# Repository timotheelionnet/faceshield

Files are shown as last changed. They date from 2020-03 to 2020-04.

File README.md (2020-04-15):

# faceshield

3D printing models for faceshields built at NYU for NYU Langone Health
These models are based on the budmen design  https://budmen.com/ with modifications 
for comfort and durability based on NYU Langone Health ICU and Emergency Medicine staff.
Design Team: Mihály Vöröslakos, Neta Agmon, Victoria Bill, Elizabeth New, Benjamin King and Timothee Lionnet based on the budmen model.

Assembly requires:
- 1 3D printed shield holder (shield_holder_nyu)
- 1 3D printed strap lock (strap-lock)
- 1 transparent shield (we have used 0.5 mm thick carbonate sheets, cut pattern in transparent_shield_cut_nyu)
- 1 elastic band (0.5" wide)
- 1 piece of foam (3/4" wide by 0.5" thick weather stripping foam; about 9" per shield)
- 4 pop rivets (1/8" diameter, 1/8" grip length)

Instructions:
- 3D print the shield holder and its strap lock. 0.3 mm thick layers, 10% infill with 2 solid layers at the top and bottom work well for us. Using a 0.8 mm nozzle reduces print time more than 2-fold compared to 0.4 mm.
- cut the carbonate sheet (following the pattern in transparent_shield_cut_nyu). We have used laser cutting and other tools.
- cut a 9" long foam strip and stick it to the inside part of the shield holder.
- using a riveter, secure foam to shield holder with four pop rivets.
- cut desired length of elastic band and tighten using the strap lock.
- wipe assembly with Isopropyl Rubbing Alcohol 70% Wipe.

Detailed Materials and Assembly Instructions are available in pdf format:
Reusable  Face Shield Assembly NYU 204_13_20.pdf

Contact/Affiliations:

Benjamin King, PhD & Timothee Lionnet, PhD
Institute for Systems Genetics & Department of Cell Biology
NYU School of Medicine
http://www.timotheelionnet.net/

Neta Agmon, PhD 
Neochromosome, Inc. 
ACLSW 14th Floor 
430 East 29th street 
New York, NY 10016

Elizabeth New & Victoria Bill
NYU Tandon MakerSpace
https://engineering.nyu.edu/research-innovation/makerspace
tandon-makerspace@nyu.edu

Mihály Vöröslakos, PhD
Neuroscience Institute, 
NYU School of Medicine

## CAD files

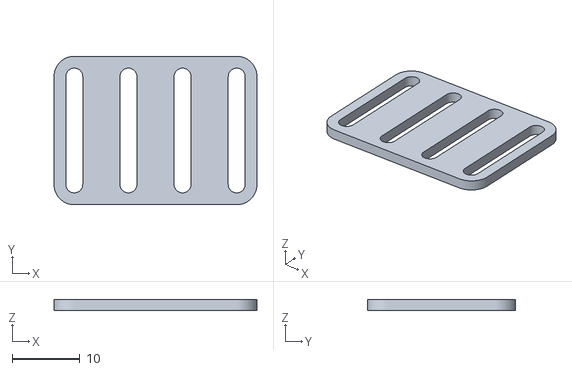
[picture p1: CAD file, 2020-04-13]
strap-lock_5_16_extended.stl
30.0 x 21.9 x 1.60

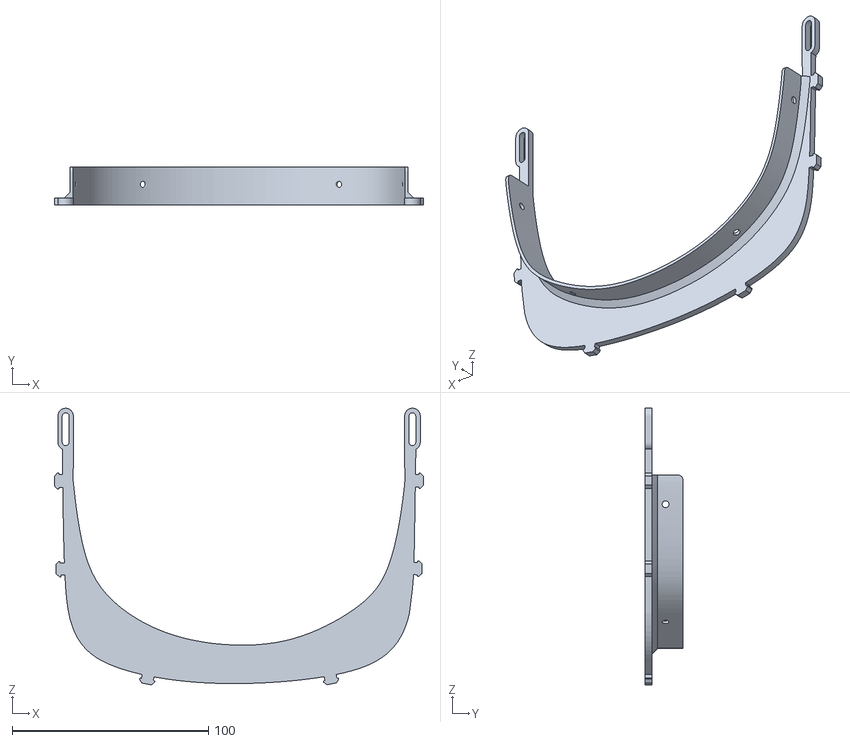
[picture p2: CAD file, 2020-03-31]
shield_holder_nyu_v3.stl
188.1 x 19.6 x 141.1

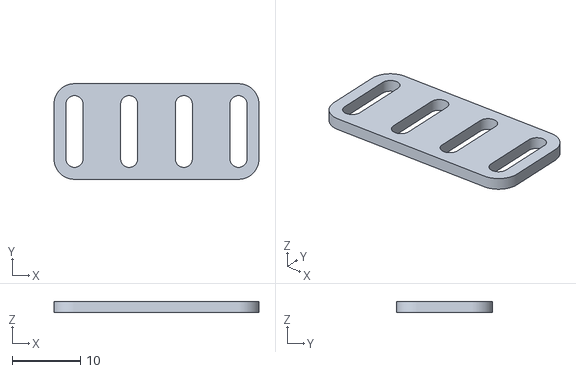
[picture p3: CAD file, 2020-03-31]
strap-lock.stl
30.0 x 14.0 x 1.60

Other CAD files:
shield_holder_nyu_v3.f3d

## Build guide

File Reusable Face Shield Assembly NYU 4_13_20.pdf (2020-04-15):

Thank you to everyone working on the shield project. Every person has contributed to protecting the lives of medical personnel working on the front line.

Allocating Materials:
Shield:
Recommended materials: Clear Polycarbonate, Duralar, clear acrylic
- Carbonate is harder to laser-cut but very clear
- Duralar is much faster to laser cut but reflections reduce visibility.
- Thickness: 0.010” or 0.020” ( “ = inch)
- Get sheets with dimensions that are divisible by shield size if you can, but supply is spotty and you may need to get sizes that leave more plastic waste than a divisible sheet.
- Laser cut to size (or cut by hand if necessary)
- Laser cut model linked here (https://github.com/timotheelionnet/faceshield/blob/master/transparent_shield_cut_nyu_v2.ai)
- Quick Dimensions: (Look at the drawing on the last page of this doc for details)
- Long side: 305 mm (~12”) before corner cuts
- Short side: 202 mm (~8”) before corner cuts
- Corner cuts on bottom: 40 mm across and down, which will reduce the short side length to about 160 mm

Visor:
3D printed from .STL model linked here: https://github.com/timotheelionnet/faceshield

Recommended Print Settings:
- Disable Raft
- Plate temperature: 55℃
- Wall thickness: 1.4 mm
- Wall count: 2
- Layer Thickness: 0.3 mm
- Infill: 10%
- 2 solid layers at the top and bottom.
- Pattern: Triangles if possible
- Using a 0.8 mm nozzle improves printing rate by more than 2-fold vs 0.4 mm

Strap:
Elastic, ½“ wide, cut to lengths of 28” (Look in hardware, or arts & crafts stores)
- Original model strap-lock.stl fits these
As of 4/13 we switched to wider elastic straps 3/4” and 5/8“
- Only the updated model strap-lock_5_16_extended.stl is suitable for these sizes

Strap Lock:
3D model is also on github (https://github.com/timotheelionnet/faceshield/blob/master/transparent_shield_cut_nyu_v2.ai)

Note previous section, use a compatible strap lock for your elastic

Foam Padding:
Material: Adhesive foam, rubber or poly
Maker: Frost King is a common brand, look for weather stripping at hardware stores mostly anywhere.
Ideal Dimensions:
- Width: ¾” wide is
- Thickness: ⅜-⅝”
- Length: 12” per unit

Glue or Rivets
- Rivets give better durability, but glue by itself is faster and satisfactory

Pop Rivets: 1/8" diameter, 1/8" grip length, and you will need a hand-held riveter (4 per unit). Parts and tool available at some hardware stores- Home Depot is best bet

Glue: Super glue. We recommend Gorilla Glue Gel which is widely available

List of Parts
1 3D printed visor
1 3D printed strap lock

### 1 transparent shield 1 elastic band 1 piece of foam

Either 4 pop-rivets or about 7 spots of glue

Assembly:
- Cut elastic bands, shields, and foam to size en mass to speed things up

### 1. Peel the covering off of the foam strips (to prevent adhesion problems later)

If you’re using rivets, go straight to step 2

If you’re using glue: dab generous, regularly spaced spots from edge to edge along where the foam is going to be adhered (and skip step 3).

### 2. Adhere foam to the visor (photos below)

Compress it long-ways as you go. The foam’s length eventually contracts, so scrunching it like this prevents it from lifting off of the plastic between adhesion points.

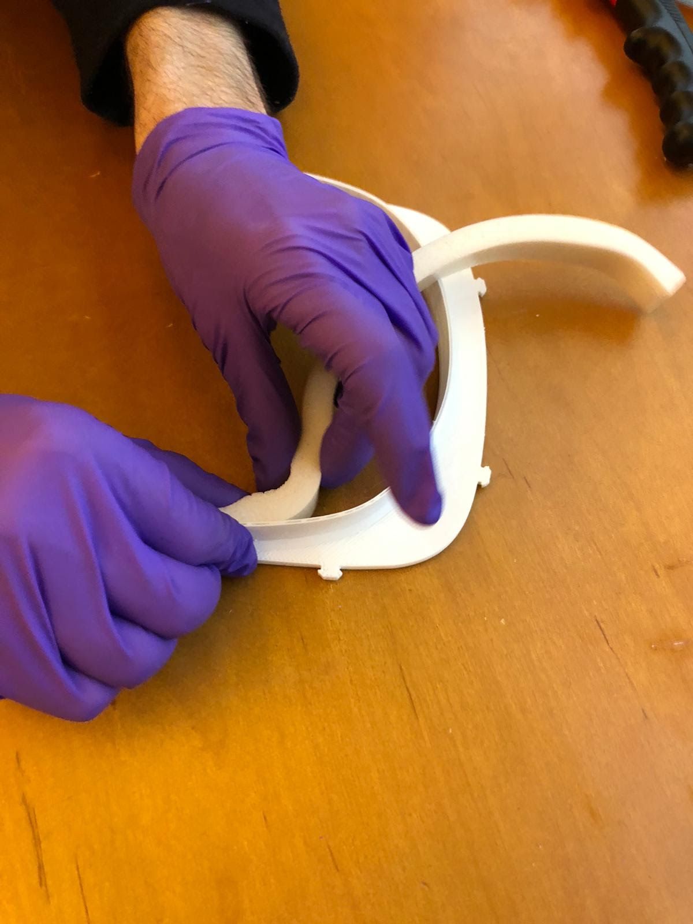
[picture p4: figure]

### 3. To rivet:

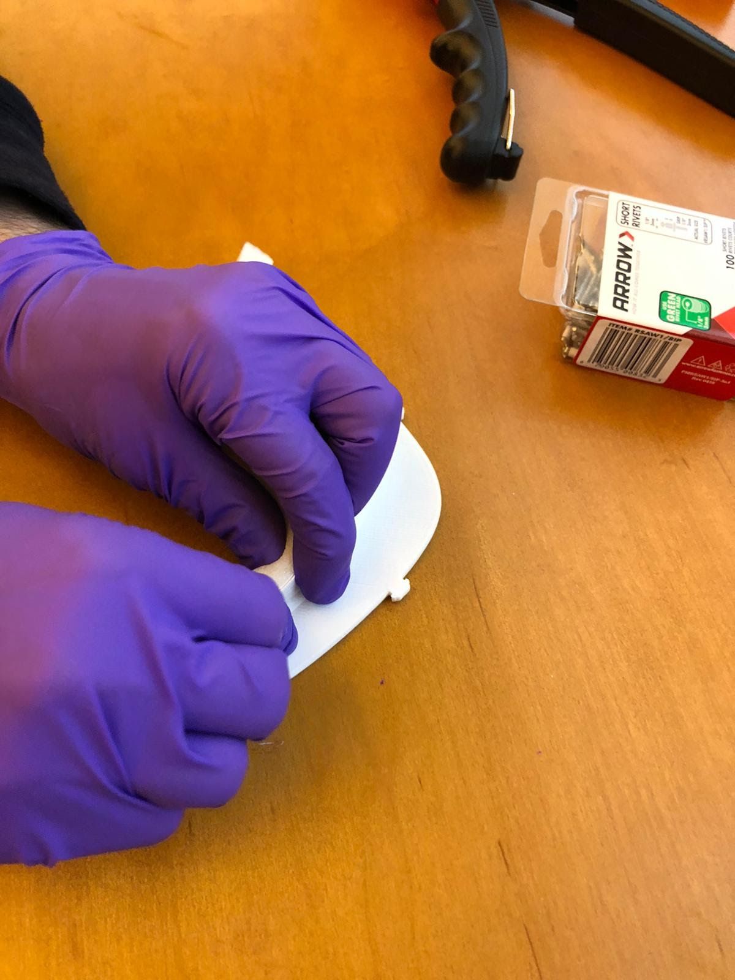
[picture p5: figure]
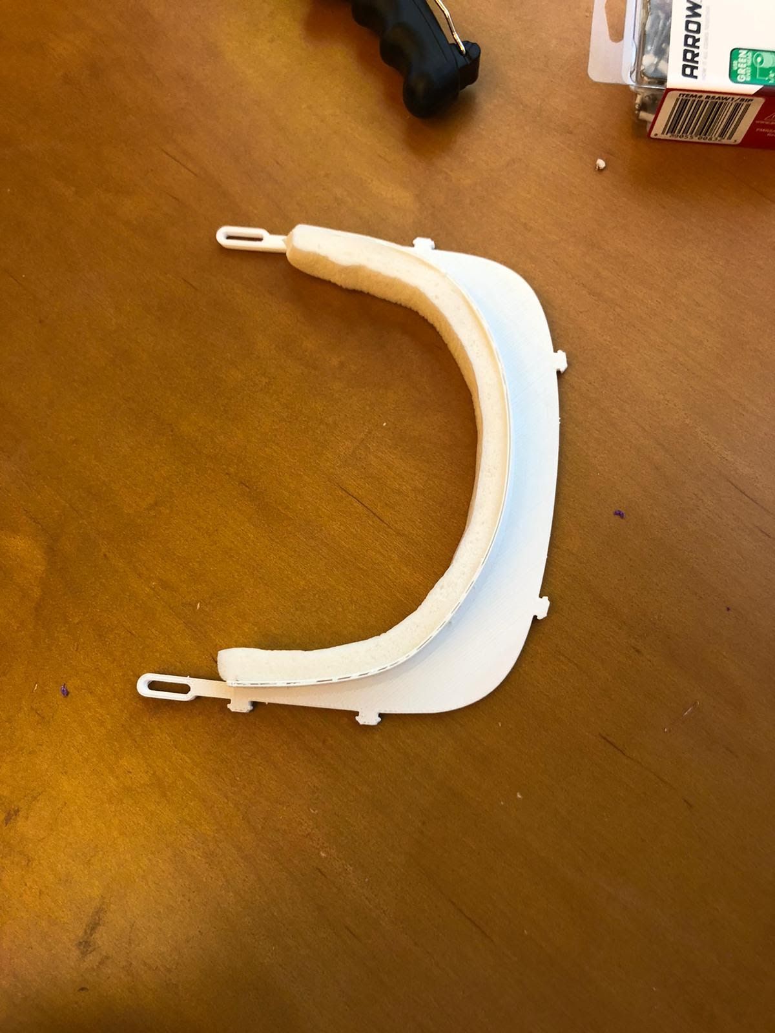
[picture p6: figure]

a. Poke holes through the foam using back-end of the rivet
b. Push the front of each rivet (with sheath) through of their hole, inside to outside.
c. Slide the riveter onto the rivet, squeeze once, then squeeze again to snap the tail of the rivet off.
- This might take more than two squeezes and that’s ok.
(a) | (b) | (c)

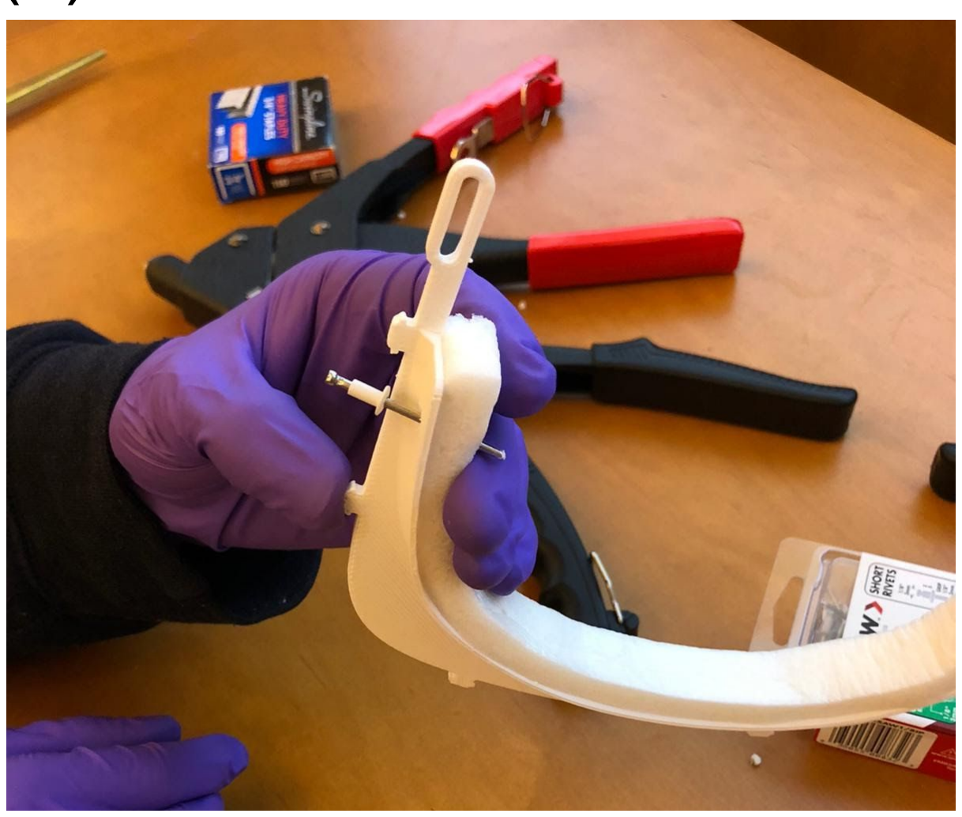
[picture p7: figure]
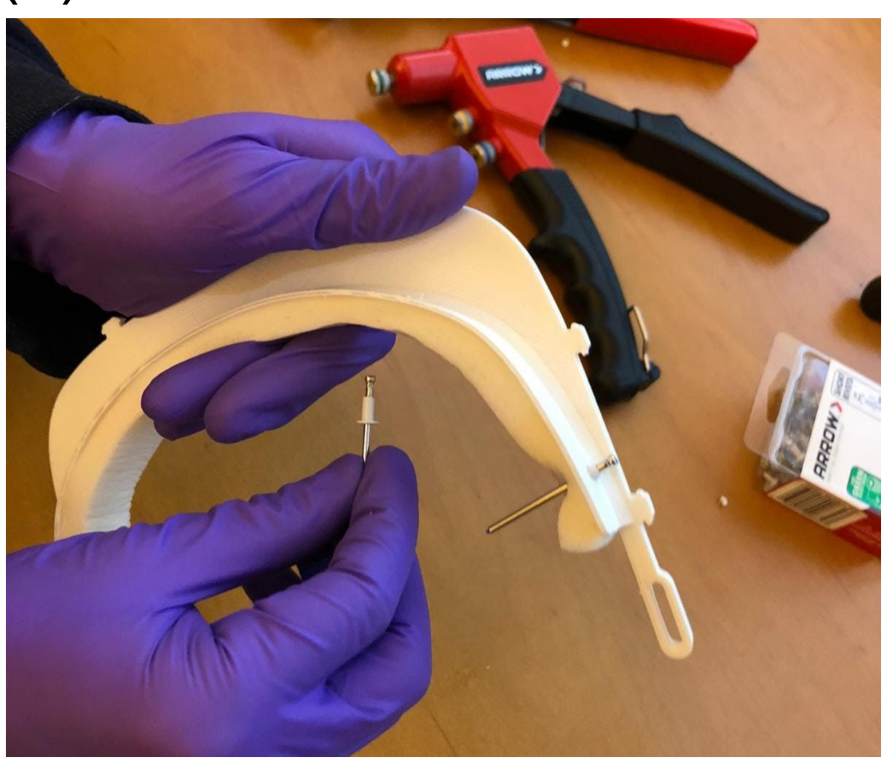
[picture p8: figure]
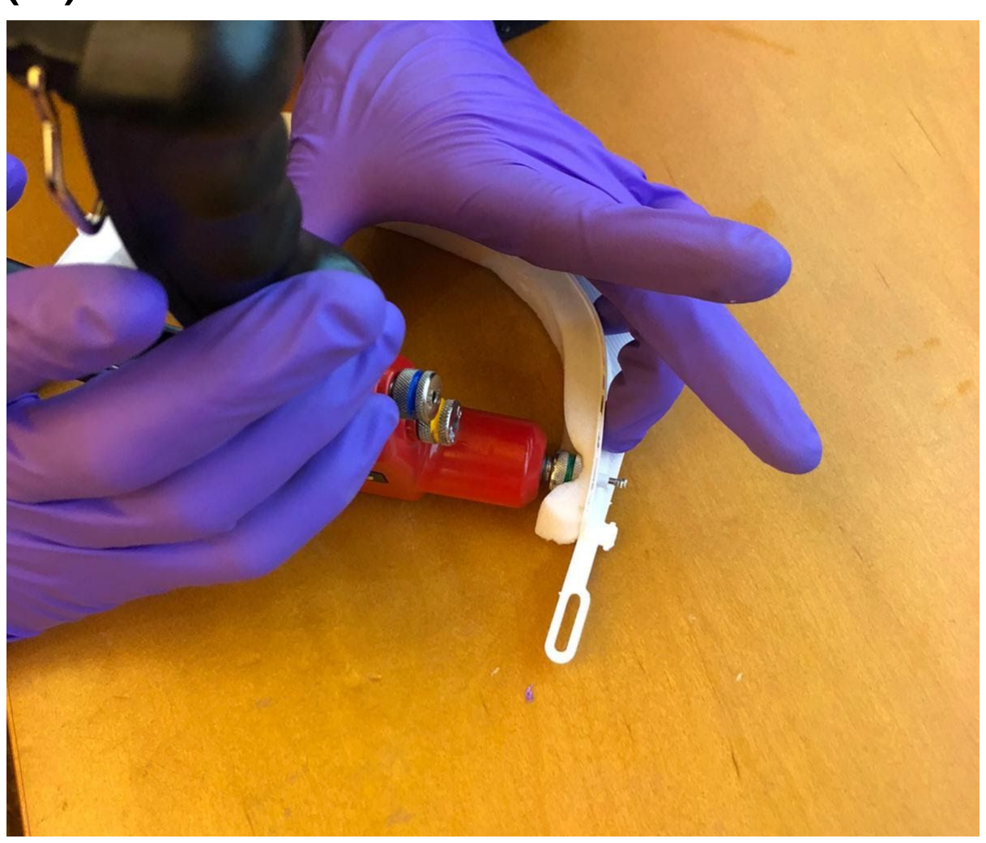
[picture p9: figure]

One completed rivet shown
here (inside, outside face):

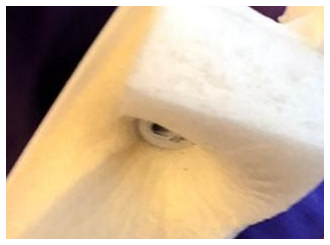
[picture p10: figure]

### 4. Attach shield to visor (photos below)

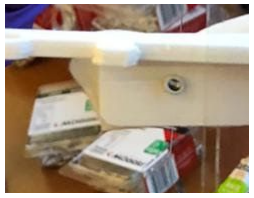
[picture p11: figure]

- There are 6 knobs on the edge of the current version of the visor which the shield should pop onto (with a fair amount of force).
- You only need to use the middle 4, as our shield is cut with only 4 holes
- The flat side of the visor should be facing up when it’s done

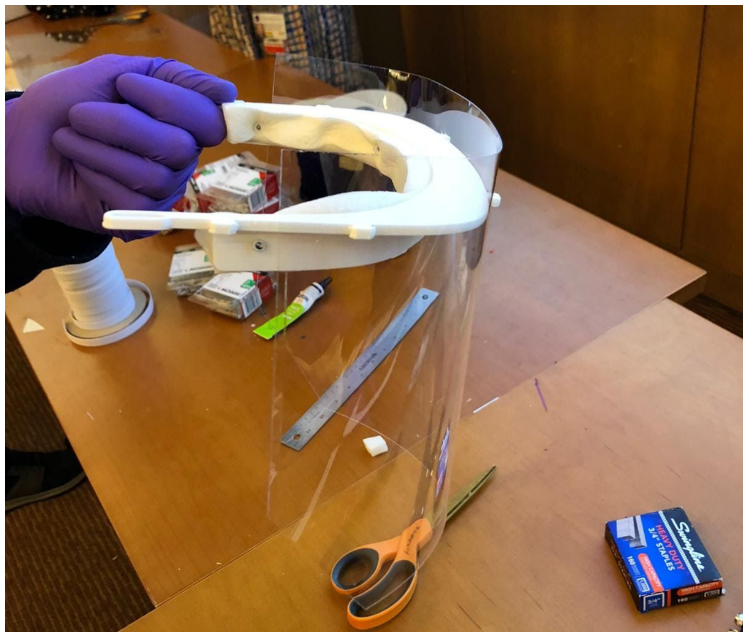
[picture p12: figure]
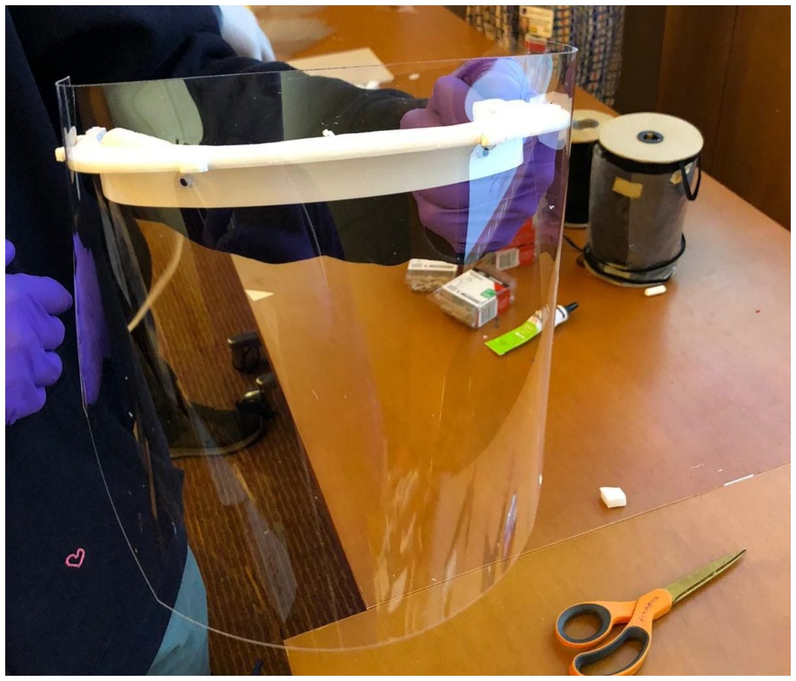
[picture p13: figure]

### 5. Feed the strap through the slots on the “back” of the visor

- Feed the ends of the elastic through a middle hole, and out the nearest outer hole

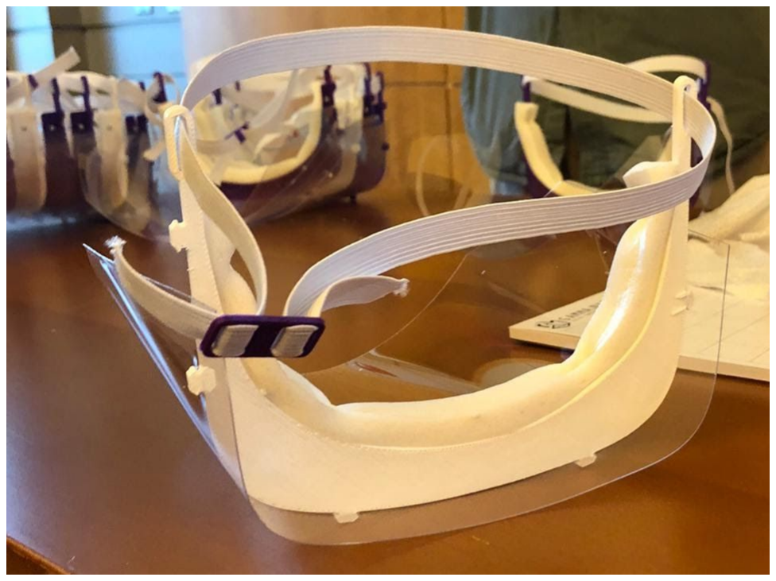
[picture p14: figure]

### 6. Wipe down the inside and outside of the shield, as well as the top and bottom of the

exposed plastic on the visor.
- Isopropyl rubbing alcohol 70% wipe, or any other CDC-recommended formulation

### 7. We package them in garbage bags in sets of 20

- This has been an efficient way to keep track of things
- We deliver our shields on foot and by car

Contact/Affiliation:
Author of this guide: Max Paukner [Department of Chemistry, NYU Graduate School of Arts and Science]

Main Organizers of Project at NYU: Benjamin King, PhD, Timothee Lionnet, PhD [Institute for Systems Genetics & Department of Cell Biology NYU School of Medicine]
(printing and assembly)
http://www.timotheelionnet.net/

Important Contacts:
Neta Agmon, PhD, Neochromosome, Inc. ACLSW 14th Floor 430 East 29th street New York, NY 10016

Elizabeth New & Victoria Bill, NYU Tandon MakerSpace
(laser cutting and printing) https://engineering.nyu.edu/research-innovation/makerspace tandon-makerspace@nyu.edu

Mihály Vöröslakos, PhD Neuroscience Institute, NYU School of Medicine

Rendering of the Clear Plastic Shield

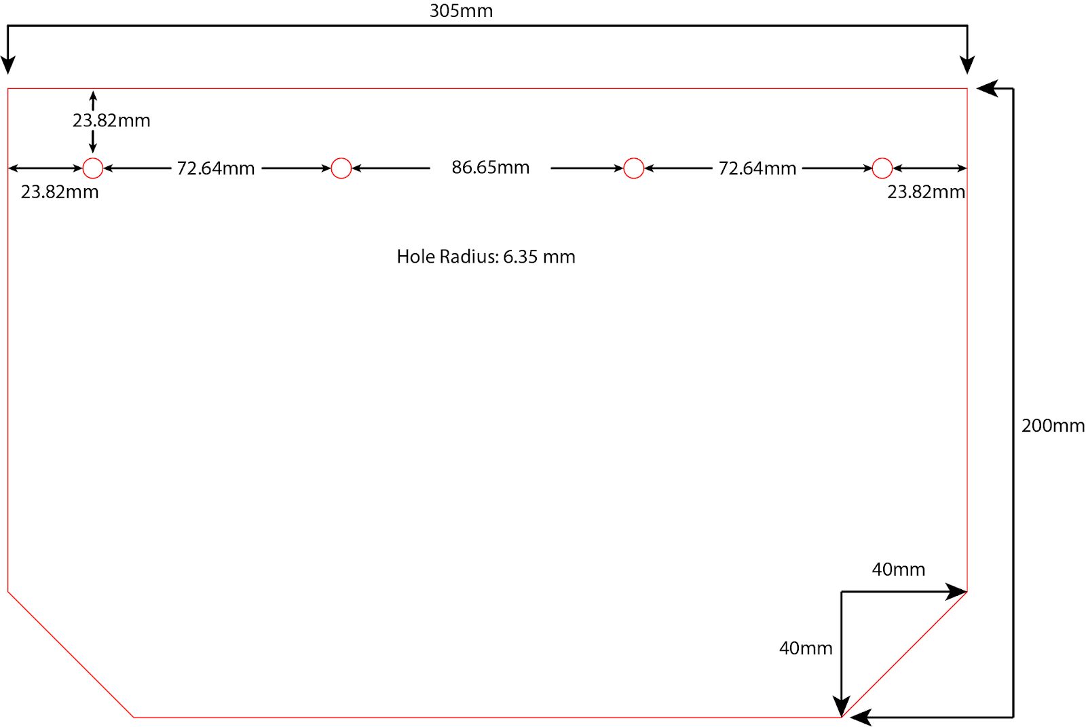
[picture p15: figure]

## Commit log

2020-03-31 Design approved by NYU Infection Prevention and Control, 3/30/2020
    [face-shield shorter bill rivets 0329 v2.f3d, face-shield shorter bill rivets 0329 v2.stl, strap-lock.stl]
2020-03-31 simplified file names
    [shield_holder_nyu_v3.f3d, shield_holder_nyu_v3.stl]
2020-04-13 included extended strap lock for wider elastic bands
    [strap-lock_5_16_extended.stl]
2020-04-15 added assembly instructions pdf
